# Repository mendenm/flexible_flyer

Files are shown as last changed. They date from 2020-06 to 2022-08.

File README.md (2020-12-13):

# The Paraglider a.k.a. Flexible Flyer

See the [progress log](progress_log.md) to see what is happening.

## NEWS!  
This project has finalized on the name "paraglider" instead of "flexible flyer".  It's the same project! I can't change the name of the git repository.

## Overview

This repository contains a couple of different but closely related, projects.  It is derived from a mix of the [Phoenix v2](https://www.thingiverse.com/thing:1453190), the [Unlimbited Phoenix v3](https://www.thingiverse.com/thing:1674320), and the [Phoenix Reborn](https://www.thingiverse.com/thing:2217431) hands.

* The big part:  fully parameterized scaling of the v2 and Reborn palms, using OpenSCAD.  
	* 	This allows the palms to be scaled independently of the hinges, so that commercial steel pins or nails can be used to make precision, smooth-operating joints.  
	* The parameters allow selection of different options for both hinge pins and for plastic tubing bearings, which make even better joints.  So far, there a designs using:
		* 	 industrial 1/16" dowel pins with Delrin tubing bearings around them
		* 	 3 mm screws with PTFE tubing for bearings
		* 	 Stainless steel finishing nails (deck nails) with PTFE tubing
 	 
		All of these options add between about $0.50 and about $2.00 to the cost of a hand. Materials sources are shown at [Joint Materials](#Joint-Materials)
	
	* The clearance on the tongue-and-groove joints is set independently of the scale of the hand.  This way, hands do not become floppier as they scale up to larger size. Also, by adjusting this spacing, there is room to insert self-lubricating plastics in the joint to lower the friction.  This will improve the grip strength.
* [A new design for supports](#New-support-system) for the big arch on all three of these palms. I am providing a completed STL file for these, along with the OpenSCAD code which converts the basic palm into the supported palm.  These supports are flying supports; they do not touch the baseplate.  They are bridged under the top of the arch, and require very little material or time to print.  They break off easily after printing, and remaining nubs can be sanded off.  
* Repaired meshes for the v2 and Reborn palms.  The meshes were run through [Meshmixer](http://www.meshmixer.com) to remove the support box, and then the remaining holes in the mesh were (mostly) closed up.  The Reborn palm, which is derived from the v2 palm, is rederived using OpenSCAD to make the modifications required.

## Parametric Scaling and modification

This is a parametric adaptation of the Phoenix Reborn hand, that allows the primary components (palm and fingers) to be scaled while holding the sizes of the connecting components (finger pins) constant,  so a standard kit of metal connectors can be used, instead of printing plastic pins to connect everything.  The OpenSCAD files allow one to select sizes for whatever connectors are to be used, and then independently scale the palm and fingers.  The connectors can be metal pins of nails, or 3mm screws.  They can have plastic tubing (Delrin or PTFE) wrapping them inside the holes in the phalanx, resulting in a very smooth-operating bearing.

The palm design is a combination of the Phoenix Reborn palm with the fused-in mesh from the Unlimbited V3 palm. This greatly reduces the number of screws required to assemble the hand.  The palm also has new 'flying supports' which solve the problem of the overhang at the top of the palm arch, without printing large support structures. If the integrated mesh is not needed, it can be disabled in OpenSCAD. 

The whole design here is to provide a flexible toolkit to create locally-appropriate variations of the hand, while letting OpenSCAD handle the scaling issues.  Many things can be commented out of the OpenSCAD code to make variations.  For example, if the fused palm mesh isn't desired, the line which fuses it in can be preceded with an asterisk ('*') which tells OpenSCAD to ignore it.  Also, if the new support structure is desired but conventional printed pins are still being used, all the fancy parametric drilling can be turned off, resulting in a (nearly) conventional Reborn hand.

The Reborn-style hand is being recreated in OpenSCAD from the Phoenix v2 palm, by redrilling the tunnels and slots, since it was possible to repair the mesh for the v2 palm to the point where OpenSCAD considered it valid (after removing the support box in MeshMixer).  It has not been possible to date to repair the Reborn palm mesh to the point at which the OpenSCAD openCGAL geometry libraries consider it valid. The file "palm\_left\_v2\_nobox.stl" contains this modified mesh.  

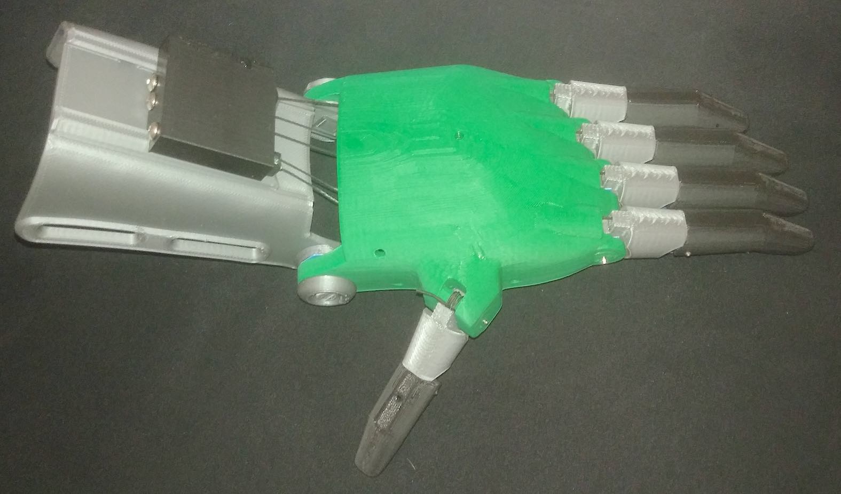
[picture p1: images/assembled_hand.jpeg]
picture of palm and fingers
 

**NOTE**:  any parts not present in the OpenSCAD files are assumed to be obtained from the Phoenix Reborn repository or the Raptor Reloaded repository, which have the gauntlet and other bits.

### Generating the parametric results
You need to run the fingerator.scad to get an STL of a set of fingers at a specific size.  Then run paraglider\_palm\_left.scad to get a hand of the same size, with the same pin specification.  In OpenSCAD, you will unhide the (normally hidden) Customizer window, which will bring up drop-down menus to set the sizes.  I usually start with 130% scale (1.3 size), which is a medium-sized hand.

The fingerator only generates one of each size finger, so for a real hand, these would be duplicated in the slicer to get appropriate numbers.  I would start just by printing one of everything, and experimenting with the parts.  The fingers are much smaller than the palm, of course, so it is not a big issue to print variations on them. Note that if the parts do not fit well, you only have to change the clearance and reprint the phalanges, since they are where the clearances are calculated in.

You also need to run gripper\_box\_pieces.scad to generate the tensioning box scaled for the thermoformed gauntlet.  This result is compatible with simply scaling whippletree\_JD3.stl to the appropriate size in the slicer.

## Joint Materials

Here is a list of sources I am using for the materials.  Variants of most of these should be available from industrial supply houses anywhere in the world. I do not endorse the sources below, but they do have stuff I need.

* 1/16" dowel pins, various lengths
	* pins [McMaster-Carr](https://www.mcmaster.com) SKUs 90145A421, 90145A422, 90145A423, 90145A425, for example. Needs 10 total, including one of the longer ones (depending on hand size) to pin the combined index and middle finger joint.  If a rotary (Dremel, e.g.) tool is available, pins can be easily cut to length.
	* 1/16" ID Delrin bearing tube McMaster-Carr SKU 8627K119, need about 2 inches to do a hand. 

* 3 mm screws
	* Screws are universally available
	* tubing any metric 3mm ID tubing or Imperial 1/8" ID tubing

* Stainless Steel nails (the cheapest option, by far!)
	* for example, [Fastener USA](https://www.fastenerusa.com/nails/hand-drive-nails/finishing/1-1-2-x-15-gauge-304-stainless-4d-finishing-nails-1lb.html).  These can be cut to length.
   * tubing for bearings can be found at (for example) [Fluorostore](https://fluorostore.com/products/fractional-metric-ptfe-fluoropolymer-tubing).  

* Side-load bearings to insert in joints if extra clearance is left in the phalanges can be obtained from [Igus](http://www.igus.com), part number A160T-5-100-G.  This item, for about $13.00, is 1 meter of 100 mm wide, 0.5 mm thick, adhesive-backed self-lubricating plastic tape.  One spool should make between 50 and 100 hands, so it adds no significant cost. Also, part number A160T-5-100 is the non-adhesive variety of bearing material, which is useful for the thermoformed wrist bearing, where there is no need for the adhesive. Use their 'search' field at the top of the page; there is almost no other way to find these on their web store.

## New support system

This support system looks like:
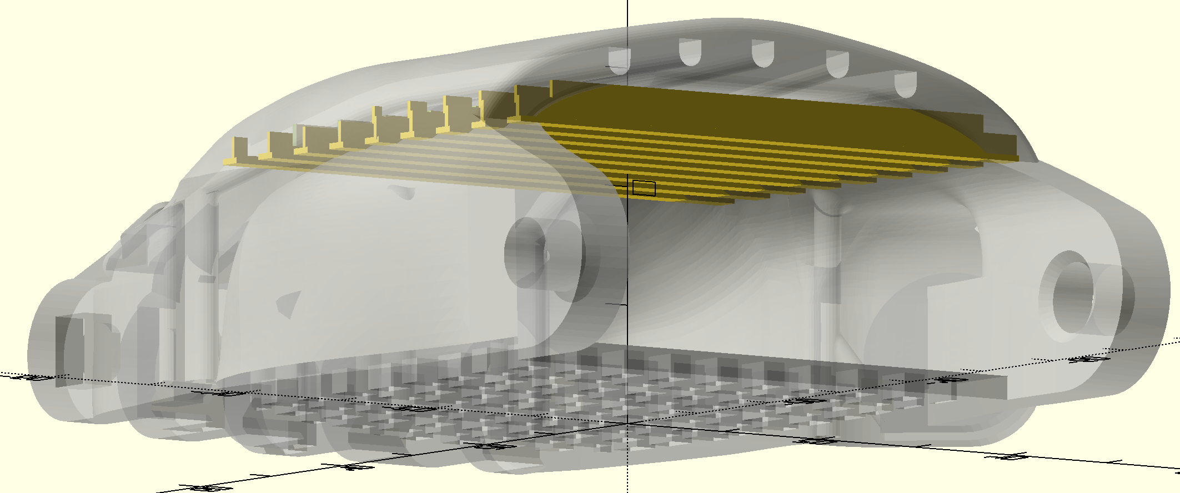
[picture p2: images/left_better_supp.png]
Rendered image of support system
  The goal is a print which is walk-away safe, which can be started, and expected to just work without any close monitoring to make sure the arch finishes safely. If you can print a half-decent bridge, these will work.  It should be printed with quite a lot of cooling, since there is still a significant overhang, but the supports start just low enough that the overhang never becomes dangerous. 

After printing, these supports snap off quite easily.  They leave small 'nubs' on the inside, which sand off very well with a rotary tool such as a Dremel tool with a flap wheel.  They can be removed by hand-sanding, too.

STL Files are provided for left-hand palm of the Unlimbited Phoenix v3, the Phoenix v2, and the regenerated Phoenix Reborn.  Just mirror these in the slicer to get the right-hand version.  Also, an OpenSCAD file for each of these is provided, to allow the supports to be adapted as needed.  The mesh for the Unlimbited palm was regenerated directly from the online Fusion360 source file, to get a higher-resolution mesh.  All of these are designed to be printed flat on the printer bed, with no supports and no raft.

# Notes from Phoenix Reborn README.txt
*Rest of the text blatantly copied from the Phoenix Reborn file*

This is a Remix of the Phoenix Hand & UnLimbited Arm, designed by Albert Fung. This project is a collaboration between e-NABLE Sierra Leone and the Hong Kong Maker Club.

It became apparent in our previous feasibility study that for the 3D printed prosthetics to survive the tropics, we need to remove components that are not well-adapted to hot weather. We therefore set out to replace all the rubber bands in the Phoenix hand.

Palm: We used the One-Arm palm designed by below_cho as out starting point. All the cable tunnels have been widened, the knuckle stumps removed, and a bar is added at the thumb base for tying elastic cord.

Palm mesh: we have modified the thick palm mesh by John Diamond to strengthen the screw holes.

Fingers: Tunnels have been created so an elastic cord can now run all the way from the finger tip up into the palm.

Pins: For snug fitting, some of the pins have been resized and reshaped.

Hope you'll find this new remix useful!

Ed Choi

## Links:

* [e-NABLE Sierra Leone - Facebook](http://www.facebook.com/enablesierraleone)
* [e-NABLE Sierra Leone - CrowdFunding](http://www.GoFundMe.com/enablesierraleone)
* [Albert Fung - designer](http://albertfung.ca)
* [Hong Kong Maker Club - collaborator](https://www.facebook.com/hongkongmakerclub/) 
* [Raise3D HK Printer - manufacturing](https://www.facebook.com/raise3dhk/)
* [Printact 3D Printer - prototyping ](http://www.printact.co)

## Print Settings

* Rafts: No
* Supports: No
* Infill: 30%
* Walls/top/bottom: 3
* Layer height: 240-320 µm from an 0.4 mm nozzle.  If adaptive layers are available, making the very top of the hand have smaller layers will result in a smoother top.

## Notes: 

For a wrist-powered prosthetic hand, please use the [Reborn Hand thermal gauntlet](http://www.thingiverse.com/thing:864030).
 and tensioner/tensioner pins from the [Raptor Reloaded](http://www.thingiverse.com/thing:596966). 

For an elbow-powered prosthetic arm, please use the Reborn palm with the "forearm" and bicep "cuff" from the UnLimbited Arm (see link). There is a glitch in the Thingiverse Customizer, so you will need to set the UnLimbited "hand length" to at least 145mm. Otherwise the forearm wrist joint would not be wide enough to fit into the palm.
 
http://www.thingiverse.com/thing:1672381
http://www.teamunlimbited.org/the-unlimbited-arm-20-alfie-edition-current/

We printed the Reborn hand at 124% and used it with parametric forearm, cuff and tensioner pins from the UnLimbited Arm(v2.0). From our field experience, the UnLimbited Arm cuff pins are not stronger enough to hold the elbow in place for very long. So we advice everyone to use Chicago/binding screws (glued) instead.

Scaling the ReBorn Hand parts at 124% would give you:

Palm width (widest): 80mm
Wrist joint (outside): 75mm
Wrist joint (inside): 64mm

## Additional materials:

* [Braided fishing line - 80lb.](http://www.ebay.com/itm/KastKing-SuperPower-Braided-Fishing-Line-330-yds-1100yds-SELECT-LB-TEST-/190909992257?var=&hash=item2c731f4d41:m:m6k91tkQ1bIzQbS8tDpHzaQ)
* Elastic cords - 1.5mm - for hands printed at 100% or above
* Screws - for tensioner block - Hands printed at 124%: 
single thread woodscrew 3.0 x 30mm
* Screws - for palm mesh printed at 124%:
Reassure R2 - full thread woodscrew 3.0 x 16mm
* Silicone fingertip grips - Tipper Lee, and superglued to secure them to the fingers
* Velcro - 1 inch thick double-sided
* [Adhesive Foam - 5mm thick](https://www.amazon.co.uk/Self-Adhesive-various-including-padding-Outfitting/dp/B002GUB9R0/ref=sr_1_5?s=sports&ie=UTF8&qid=1491140349&sr=1-5)
* 13mm binding screws for the elbow joints (use superglue or Loctite to prevent loosening). 
* [Loctite 243 seal thread](http://www.ebay.com/itm/121826873262?_trksid=p2057872.m2749.l2648&ssPageName=STRK%3AMEBIDX%3AIT)

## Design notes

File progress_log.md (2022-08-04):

# The Paraglider Progress Log
## Summer 2022
Wow! Just Wow.  An Eagle Scout project was developed to  produce detailed documentation for this, in the form of a PDF user manual, and a brief video to show how to work with OpenSCAD on these files.  Thanks to Peter Ilyin and his crew!  See the [manual](Instruction\_manual\_rev2.pdf) and [video](images/Instructional\_Video\_Trim.mp4).

* *Peter Ilyin* - Project Lead, Eagle Scout Candidate
* *Jackson Rodgers* - General Volunteer, Volunteer Coordinator, Technical Support Volunteer, Technical Writer, and Illustrator.
* *Leonard Katowitz* - General Volunteer, Printer Assistance, Photographer, and Illustrator
* *Dean DeSeve* - General Volunteer, Technical Writer, Photographer, and Illustrator
* *Mark Dorazelski* - General Volunteer, Technical Writer,  and Technical Consultant
* *Jasper Mosely* - Technical Consultant, and Digital Design Consultant
* *Albert Z* - General Volunteer, Instructions Tester
* *Thomas H* - General Volunteer, Instructions Tester
* *Dalton S* - General Volunteer, Instructions Tester
* *Indigo S* - General Volunteer, Instructions Tester
* *Chris S* - General Volunteer, Instructions Tester
* *Rick Y* - General Volunteer, Instructions Tester
 
## Mid-December 2020
### Wrist joint
The work on a wrist joint using an m3 screw instead of a plastic pin
is complete.  The joint has a conical thrust/axial bearing printed
in, so the screw is not the actual bearing.  It can be assembled
without any bearing material, or can either have something like
polypropylene sheet inserted to lower friction, or it can use the
non-adhesive Igus A160T-5-100 plastic, described in the materials list.  If using the
Igus plastic, I have included an option to print a thermoforming jig
which allows the plastic to be heated, and then stamped and drilled
using the jig.

### Labeling text
To allow hands to be traced and recorded, I have added the ability
to print 3 lines of text on the inside of the hand. These might
include the maker name, a serial number, and a date.
Whatever you want...

### Here it is
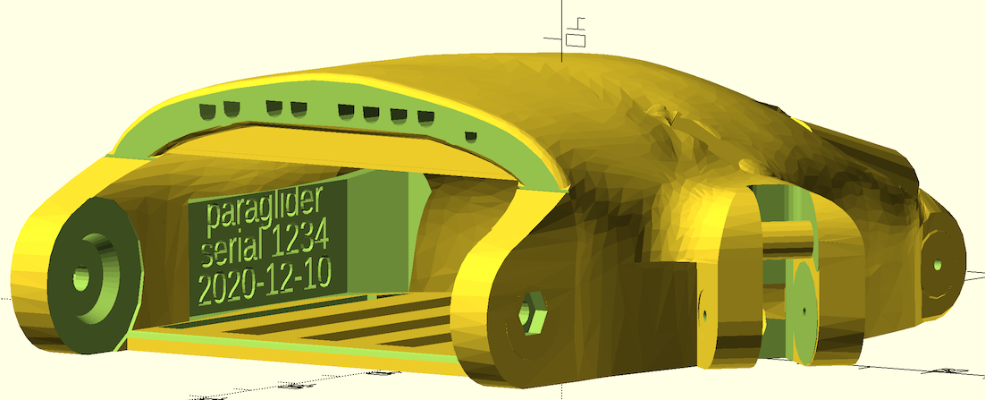
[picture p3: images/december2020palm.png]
Hand with new bearings and text

This shows the current wrist and text design.

## Early November, 2020

### Name change (sort of) to "paraglider"
It has been decided that this project will adopt the "paraglider" name, since "flexible flyer" makes it appear it might be a flexure-joint based project.  Some files and materials will keep the old name, though.

### New!  Unlimbited V3 palm 
It is now also possible to build the parametric palm against the [Unlimbited Phoenix V3](https://www.thingiverse.com/thing:1674320)  palm, which is somewhat different.  Everything works almost the same, but the passages (especially the thumb string) are quite different. Everything should be compatible, although I have not yet tested the thumb.  The positioning of the thumb socket is different on this palm, and it may require a slightly different parametric scaling of the thumb. Use paraglider_palm_unlimbited_v3.scad and its customizer script to use this.

### Reborn palm progress
Much cleanup has been carried out on the palm based on the Phoenix Reborn project.  

## Later October, 2020
The entire 'fingerator' module has been replaced. The original used a slice off of the Phoenix finger meshes to start with, and edited from there.  The new fingers are entirely OpenSCAD objects.  
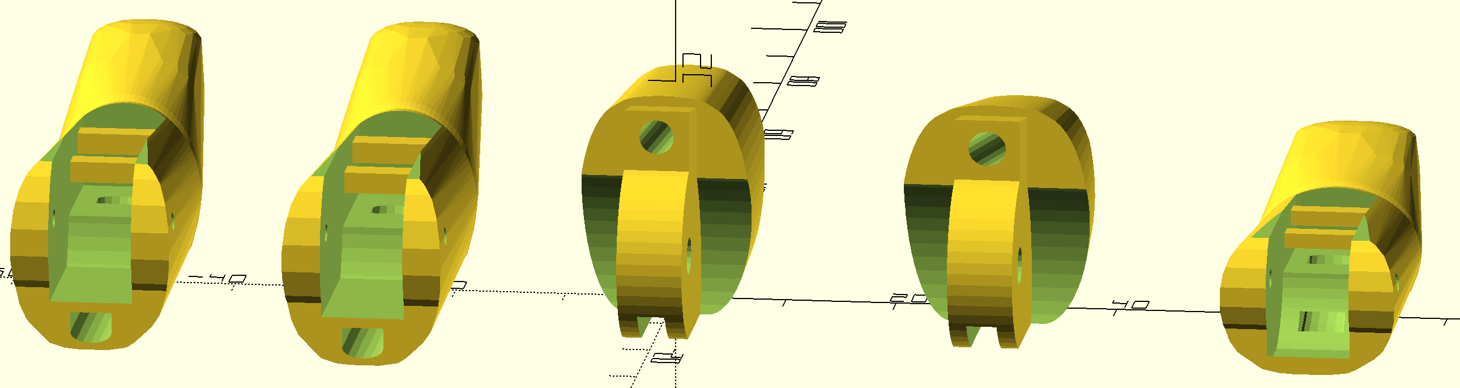
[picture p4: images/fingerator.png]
Rendered image of new fingers
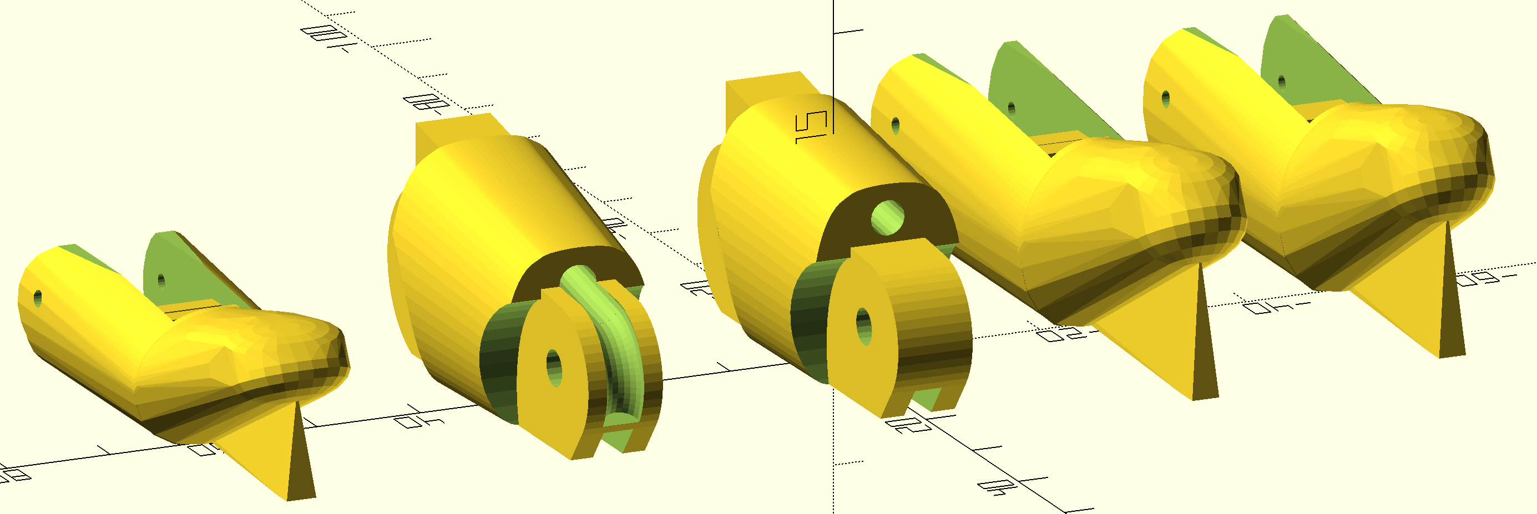
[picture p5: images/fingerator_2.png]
Rendered image of new fingers
   They have the following improvements:

* A 'keel' on the overhang to make it _really_ easy to print.  Even without very good cooling,  the distal segment overhang comes out smooth. The keel is easy to break off, and sand the stub away.
* The entire path for the elastic is covered, resulting in better aesthetics. The elastic now passes through from the top of the finger to the bottom, where it gets tied.
* There is a channel to guide the elastic so that it can be inserted in most cases without any  sort of leader to push or pull it through.
* There are two bars under each finger to tie things to, one for the string and one for the elastic.

The goal of these efforts is to produce a hand which gives as stronger grip with less effort from the user, to assist people who do not have a lot of wrist strength.

Here is a picture of an assembled finger, showing the blue Igus self-lubricating tape, the off-white bearing tubing inside a joint, and the assembled joint with a 1/16" steel pin.
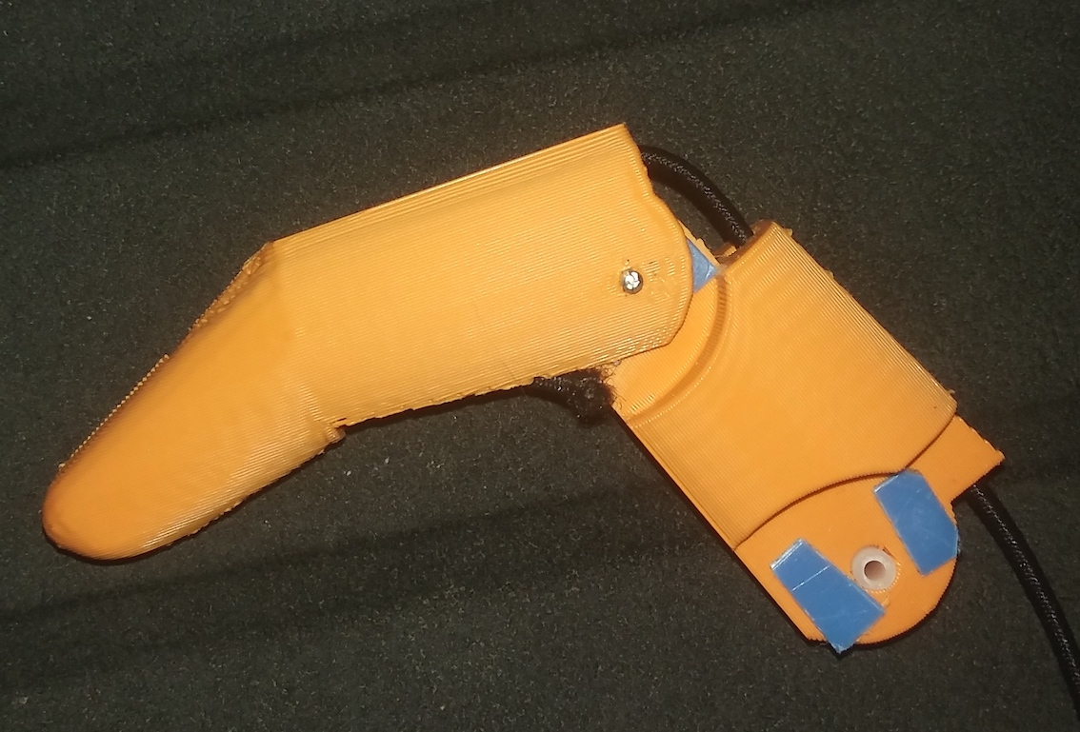
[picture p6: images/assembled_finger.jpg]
 

## October, 2020 update
There is a new OpenSCAD file, paraglider\_palm\_new\_channels.scad.  This file has a better mechanism for filling in the old string channels to get rid if various voids, etc.  It then implements an entirely new system for the channels.  There are two channels for each digit (except the thumb): one for the string and one for the elastic return band.  This should make it easier to thread, using a piece of wire as a leader to puller the strings through. It should also eliminate drag between the two lines. 
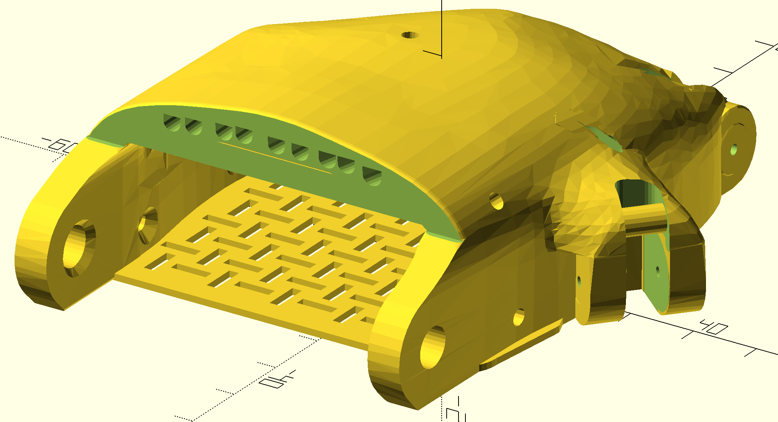
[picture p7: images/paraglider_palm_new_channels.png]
Rendered image of new channels


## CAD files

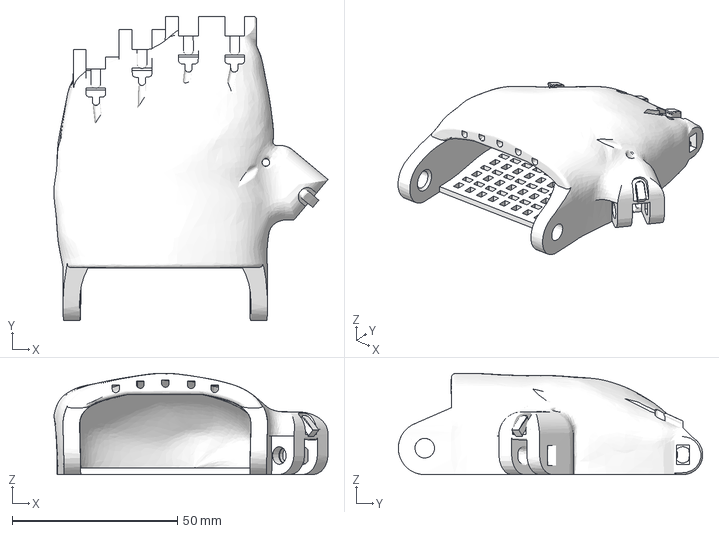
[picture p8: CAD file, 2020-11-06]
files/palm_v3.3mf
82.8 x 92.0 x 30.6 mm

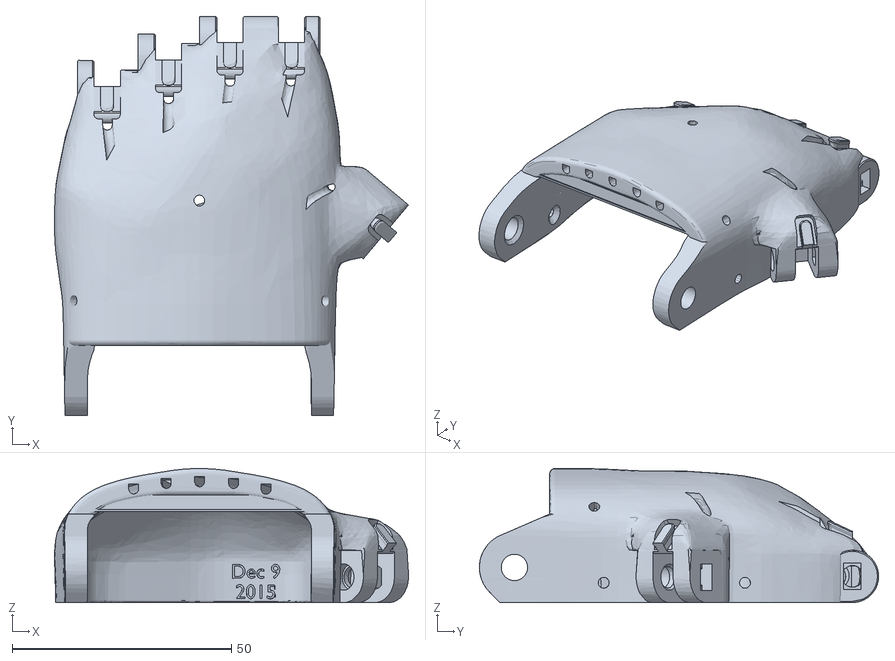
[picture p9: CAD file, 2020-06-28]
files/Phoenix_v2_new_supports.stl
80.6 x 91.0 x 30.6

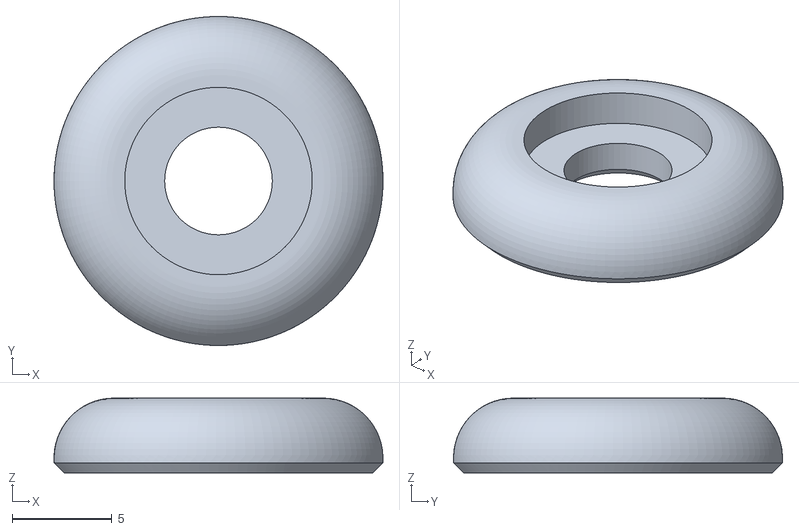
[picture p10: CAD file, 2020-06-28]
files/Reborn_elbow_pin_cap.stl
16.5 x 16.5 x 3.75

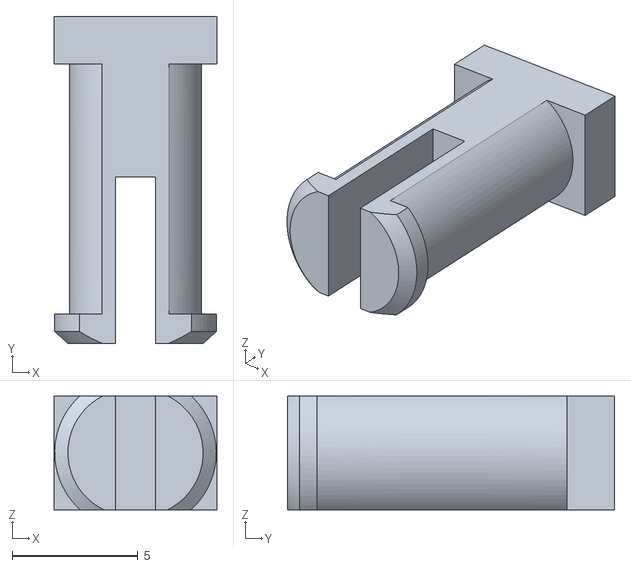
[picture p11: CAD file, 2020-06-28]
files/Reborn_wrist_pin.stl
6.46 x 13.0 x 4.51

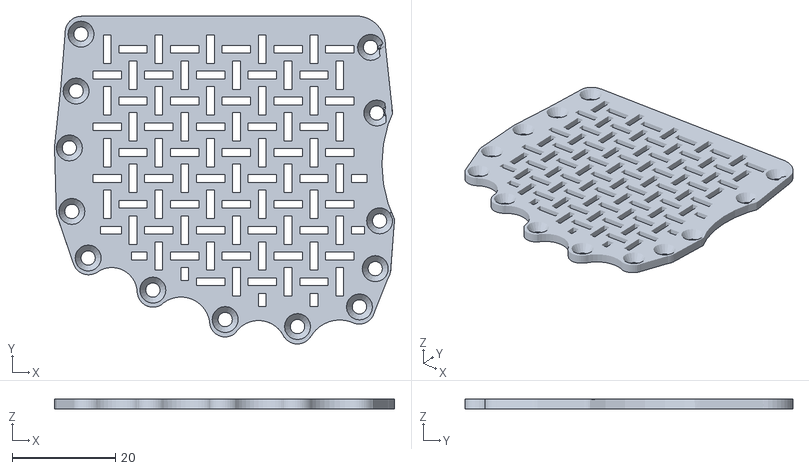
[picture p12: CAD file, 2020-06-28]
files/reborn_palm_mesh_thick_left.stl
65.8 x 63.4 x 2.00

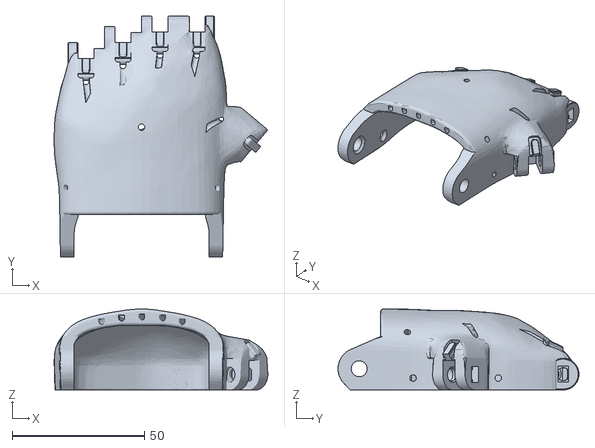
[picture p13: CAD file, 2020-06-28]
files/palm_left_v2_nobox.stl
80.6 x 91.0 x 30.6

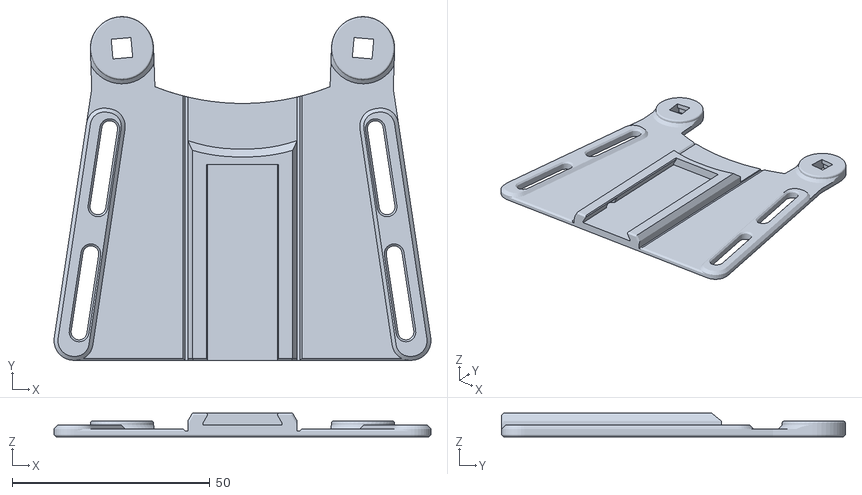
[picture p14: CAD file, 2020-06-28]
files/thermo_gauntlet_two_strap_one_row.stl
95.4 x 87.0 x 6.00

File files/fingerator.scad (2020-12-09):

/*
Parametric Finger Generator for Phoenix-reborn hand converted to paraglider/flexible flyer.
This takes a fully OpenSCAD-modelled finger, based on the general geometry of the Phoenix Reborn,  
in a manner that scales the holes to a chosen size indepenedent of the finger size.
This allows one to use a wide variety of commercial metal fasteners in lieu of 3d printed pins
to create the pivots for fingers.  

The designs in the default version of this files are set up
to use 3mm screws, 1/16" steel pins, or 13 ga (0.092") (USA) nails, with a plastic tubing
bearing on the outside to make it move smoothly.  The pins and nails may not need the tubing,
and parameters can be adjusted to make this the case. 

By manually adjusting the lines
  pivot_dia= pivot_array[pivot_size_index];
  pivot_pin_dia=pin_array[pivot_size_index];
at the bottom, to put in actual numbers instead of the pre-packaged values,
almost any geometry can be created for regions with different (e.g. metric) pins or nails.

Note that the parameters can be adjusted for your printer tolerances.  Mostly, you probably
only have to reprint the phalanx parts to adjust the joint quality, since they are the part that 
includes the hole for the pivot, and that has a clearance for the slots.  
The line
  nominal_clearance=0.6;
sets the looseness of the slots for the joints; making it smaller makes joints tighter.
Since this is cut parametricall after the scaling is done, once you have found a good value
for your printing setup, it should work for all sizes of hands, instead of getting looser
as the hands get bigger.

Marcus Mendenhall, 5 June, 2020, Germantown, Maryland, USA

*/

// size of fingers. should match scale of hand they are being printed for.
global_scale=1.25; // [1.0:0.01:2.0]
// Clearance on sides of tabs.  increase for looser fit. This only affects the phalanges, so a bad fit does not require reprinting  anything else.
nominal_clearance=0.5; // [0.1:0.01:3]

/* [Items to print] */
print_long_fingers=true; 
print_short_fingers=true; 
print_finger_phalanx=true; 
print_thumb=true;
print_thumb_phalanx=true; 

/* [Igus Bearing Material] */
bearing_pocket_diameter=0; // [0,5,7,9,11,13,15]
bearing_pocket_depth=0.4; // [0.2:0.05:0.6]

/* [Pin Style Selection -- select one] */
// choose the type of steel pin for the joints
pin_index=1; // [0: 3mm screws, 1: 1/16 inch pins with bearing, 3: 1/16 pins with no bearing, 2: 13ga finishing nails] 
// tie string onto another steel pin if true, otherwise use plastic bars
pins_for_string=false; // [false:plastic bars for string, true: steel pins for string]
    
// Extra clearance for pins to adjust for printer differences to make pins reasonably tight fits. Note that this affects all joints, so it should be pre-tested on something small like a finger in advance.
pin_diameter_clearance = 0; // [-1:0.01:1]

screws = (pin_index==0);

/* [Hidden] */
// 3mm screws with 3/16" OD delrin rod
pivot_dia_3mm_screw=25.4*(3/16)+0.25; // 3/16" OD delrin tubing with a little clearance since they were too small otherwise
pivot_pin_dia_3mm_screw=3+0.1; // 3 mm screws

// 1/16" pins with 1/8" OD delrin rod
pivot_dia_8th_delrin=25.4*(1/8)+0.25; // 1/8" OD delrin tubing with a little clearance since they were too small otherwise
pivot_pin_dia_16th_pin=25.4*(1/16)+pin_diameter_clearance; // 1/16" steel pin
// with no delrin tubing, leave extra clearance for holes in phalanges for pins
pivot_pin_dia_16th_pin_clearance=pivot_pin_dia_16th_pin+0.3;

// 13-gauge nails
// https://www.fastenerusa.com/nails/hand-drive-nails/finishing/2-x-13-gauge-304-stainless-6d-finishing-nails-1lb.html
// and 3/32" ID/ 5/32" OD PTFE tubing
// https://fluorostore.com/products/fractional-metric-ptfe-fluoropolymer-tubing
// part number F015137
pivot_dia_13ga_nail=25.4*(5/32)+0.25; // 5/32"" OD PTFE tubing with a little clearance since they were too small otherwise
pivot_pin_dia_13ga_nail=25.4*0.095+pin_diameter_clearance; // 13 ga nail

pivot_array=[pivot_dia_3mm_screw, pivot_dia_8th_delrin, 
    pivot_dia_13ga_nail, pivot_pin_dia_16th_pin_clearance, ];
pin_array=[pivot_pin_dia_3mm_screw, pivot_pin_dia_16th_pin, 
    pivot_pin_dia_13ga_nail, pivot_pin_dia_16th_pin,  ];

pivot_size_index=pin_index;

pivot_dia= pivot_array[pivot_size_index];
pivot_pin_dia=pin_array[pivot_size_index];


/* [Misc] */
// size fo m3 standard nut across flats
nut_size=5.5; // m3 nut across flats, fairly tight fit

bolt_head_dia=5.5+0.3; // loose clearance for m3 bolt head
nominal_slotwidth=6+0; // make an equation to hide from customizer
adjusted_tabwidth=nominal_slotwidth-nominal_clearance/global_scale;
adjusted_slotwidth=nominal_slotwidth;

initial_rotation=33.5+0; // hidden from customizer

module fingertip() {
    cyl_1_dia_1=11;
    cyl_1_dia_2=9;
    cyl_1_hgt=15;
    cyl_1_rot=atan((cyl_1_dia_1-cyl_1_dia_2)/cyl_1_hgt/2);

    sph_1_dia=cyl_1_dia_2-2;
    scale([1,1.15,1]) hull() {
        translate([0,cyl_1_hgt/2,(cyl_1_dia_1+cyl_1_dia_2)/4]) rotate([-90-cyl_1_rot,360/20/2,0]) 
            cylinder(d1=cyl_1_dia_1, d2=cyl_1_dia_2, h=cyl_1_hgt, center=true, $fn=20);
        for(dx=[-1,1]*0.5) translate([dx,cyl_1_hgt+2.4,sph_1_dia*0.8/2-0.0]) scale([1,1,0.8]) 
            sphere( d=sph_1_dia,$fn=20);
        for(dx=[-1,1]*0.5) translate([dx,cyl_1_hgt,sph_1_dia*0.4/2]) 
            rotate([-40,0,0]) scale([1,1,0.4]) translate([0,-1,13]) 
            sphere( d=sph_1_dia,$fn=20);
        for(dx=[-1,1]*0.3) translate([dx,0,0]) 
            translate([0,11,8.1]) rotate([-10,0,0]) scale([1,1,0.5]) sphere(d=8, $fn=20);
        rotate([90-initial_rotation,0,0]) translate([0,7,0]) scale([0.85,1,1]) 
        rotate_extrude(angle=180, $fn=90) translate([5,0]) circle(d=3, $fn=20);
    }
}

module carpal() {
    translate([0,-5.4,10.5]) rotate([-90-initial_rotation,0,0]) hull() {
        translate([0,0,-16]) linear_extrude(height=0.1) hull() {
                translate([ 4.,0,0]) scale([0.3,1]) circle(d=12);    
                translate([-4.,0,0]) scale([0.3,1]) circle(d=12);
                translate([0,-7.0]) scale([1,0.2]) circle(d=16*0.4);
                translate([0, 7]) scale([1,0.2]) circle(d=16*0.4);
        }
        translate([0,6,10]) linear_extrude(height=0.1) 
            projection(cut=true) rotate([90+initial_rotation,0, 0]) fingertip();
    }
}
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

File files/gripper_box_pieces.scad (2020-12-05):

// parts for flexible-flyer parametric variant of Phoenix Reborn

// this should match the scale of the hand and gauntlet
global_scale=1.25; // [1:0.01:2]

// this sets how much clearance is on the dovetail.  It shouldn't depend on the scale
slide_clearance=0.2; // [0:0.01:0.5]

// The (approximately) root diameter of the screw thread for a nice fit
screw_thread_dia=2.8; // seems to work for m3
screw_clearance_dia=screw_thread_dia+0.5;
// diameter of screw head
screw_head_dia=5.5; // m3 screw
// distance between edge of screw heads and slider rail
screw_head_clearance=1.0; // minimum distance of screw heads above slider rail

module slide(grow) {
    // make a scalable slide profile, inset by the specified amount for clearance
    union() {
        hull() {
            translate([0,6.65]) square([20+grow,0.70], center=true);
            translate([0,4.3]) square([17+grow,0.5], center=true);
        }
        translate([0,4.5]) square([17,5], center=true);
    }
}

module box() {
    cl=slide_clearance/global_scale;
    difference() {
        linear_extrude(height=28) union() {
          square([30,8], center=true);
          slide(grow=-cl);
        };
        whip_box_x=11.2+cl;
        whip_box_y=5;
        
        translate([-1.8,6.0-whip_box_y/2+cl,22]) 
            cube([whip_box_x,whip_box_y,40], center=true);


        piv_box_x=22.0+cl;
        piv_box_y=5.4+cl;
        
        translate([-3,2.5-piv_box_y/2,22]) 
            cube([piv_box_x,piv_box_y,40], center=true);
        
        thumb_pin=4.8+cl;
        translate([11.5,0,22]) 
            cube([thumb_pin,thumb_pin,40], center=true);
        
        
        for(dx=[[11.5,0,0],[-4.6,4.2,0],[1,4.2,0]]) translate(dx)
            cylinder(d=screw_clearance_dia/global_scale+.25, h=40, $fn=20, center=true); 
    }
}

module thumb_tensioner() {
    // translate([-15.0,69.8,-25.5]) import("thumb_v2_tensioner_pin.stl", convexity=10);
    translate([0,0,2.4]) difference() {
        rotate([-90,0,0]) intersection() {
            cube([4.8,4.8,20.5], center=true);
            rotate(45) cube([4.8*sqrt(2)-0.5, 4.8*sqrt(2)-0.5, 45], center=true);
        }
        translate([0,-3,0])
            rotate([90,0,0]) 
                cylinder(d=screw_thread_dia/global_scale, h=15, center=true, $fn=20);
        // translate([0,8,0]) cylinder(d=2, h=15, center=true, $fn=20);
        translate([0,10.3,0]) scale([1,1.2,1])
            rotate([0,90,0]) rotate_extrude(angle=180, convexity=10, $fn=50) 
                translate([-2.5,0]) circle(d=2.5, $fn=20);
    }
            
}

module pivot() {
    translate([0,0,3.5/2]) {
        difference() {
            translate([0,0,0]) cube([11,20,3.5], center=true);
            for(dx=[-2.8,2.8]) translate([dx,0,0]) rotate([90,0,0]) 
                cylinder(d=screw_thread_dia/global_scale, h=50, center=true, $fn=20);
        }
        translate([-1.1,3,1.74]) difference() {
            cylinder(d=6.5, h=5, $fn=20);
            scale([1,0.3,1]) translate([0, -10*sqrt(2)/2,0]) rotate(45) cube([10,10,12], center=true);
        }
    }
}

module whipple_tree() {
    // %import("whippletree_JD3.stl", convexity=10); 
    thickness=5.4-slide_clearance/global_scale;
    ht=thickness/2;
    difference() {
        linear_extrude(height=thickness) difference() {
            hull() {
                $fn=20;
                translate([0,-3.8,0]) circle(d=7);
                translate([6.3,1,0]) circle(d=8);
                translate([-6.3,1,0]) circle(d=8);
            }
            difference() {
                translate([0,-1]) circle(d=9);
                translate([0,-9]) rotate(45) square(5);
            }
        }
        for(dx=[-1,1]*5.3) translate([dx,5.2,ht]) scale([0.7,1,1])
            rotate_extrude(angle=360, $fn=50) translate([5,0]) 
                scale([1/0.7,1]) circle(d=2, $fn=16);
    }
}

scale(global_scale) translate([-5,-15,0]) rotate(0) pivot();

scale(global_scale) translate([5,-15,0]) rotate(0) thumb_tensioner();

scale(global_scale) box();

translate([0,15*global_scale,0]) rotate(180) scale(global_scale) whipple_tree();

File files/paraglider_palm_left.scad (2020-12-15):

inch=25.4*1; // hidden from customizer by equation, useful for pins
/* [Main setup] */
// size of hand relative to tiny 100% model
overall_scale=1.25; // [1.0:0.01:2.0]
// mirrored for right-hand?
mirrored=false; // [false:left, true:right]
// an identifying string for this hand, i.e. build date, builder, serial, etc. (15 characters/line max)
serial_line1="paraglider"; // 15
serial_line2="serial 1234"; // 15
serial_line3="2020-12-10"; // 15
// include a stamping die for thermoforming 0.5mm thick Igus bearing plastic for wrist
include_wrist_stamping_die=true; // [true: die included, false: no die]
/* [Structural parameters] */
// size of pivot pins
pivot_size=1.5875; // [1.5:metric 1.5, 1.5875:16th inch, 3.0:3mm screw]
// extra clearance for pivots to adjust for printer tolerances
pivot_extra_clearance=0; // [-0.5:0.01:0.5]
// drill holes for steel pins
pins=true; // [1:steel pins, 0: plastic pins]
// create plugs for steel pins, or leave old holes for plastic pins 
plugs=true; // [1:steel pins, 0: plastic pins]
// include fused-in palm mesh?
include_mesh=1; // [0:standard mesh, 1:simplified mesh]
// include nice covers for knuckles
include_knuckle_covers=true;
// set size of channels for strings
string_channel_scale=0.9; // [0.5:0.05:1.0]
// set size of channels for elastic
elastic_channel_scale=0.9; // [0.5:0.05:1.5]
// even if using steel pins on the fingers, use plastic pins on the wrist if old-style
old_style_wrist=false; // [true:old style, false:m3 wrist screws]
/* [Development] */
// make main object a ghost for debugging
main_ghost=false; // [1:ghost, 0:real]
// leave out string channels in preview, for much faster viewing
fast_preview=false;

use <pipe.scad>
module channel(waypoints, shapescale=1, bendradius=5, 
    fix_translation=true) {
    // the bends work best if the primary length is along 'x' here,
    // but the hand is along 'y', 
    // so we will adjust the coordinates, 
    // and then re-rotate the whole thing
    shape=[[-1.5,-1],[1.5,-1],
        each 1.5*[for(th=[0:30:179]) [cos(th), sin(th)]]
    ]*shapescale;
    path=[for(w = waypoints) 
        [0,[w[1],-w[0],w[2]],1,
            -90+((len(w)==4)?w[3]:0)]];
    // note: do a translation so that the curved _bottom_ of the pipe is
    // invariant under scaling, relative to its position when scale=0.9.
    // This is for historical continuity
    y_trans=fix_translation?1.5*(shapescale-0.9):0;
    translate([0,0,y_trans]) rotate(90) multi_pipe([shape], 
        smooth_bends(path, 2, bendradius));
}

module supports() {
    for(dy=[-29:5:10]) translate([0,dy,0]) {
        translate([-7,0.5,21]) cube([52,2,0.5],  center=true);
        translate([-7,0,22]) cube([52,0.4,2],  center=true);
        // translate([-7,0,22]) cube([45,0.4,3],  center=true);
        translate([-7,0,23]) cube([45,0.4,3],  center=true);
        translate([-7,0,23]) cube([30,0.4,3],  center=true);
    }
}


// plug up all holes and slots which need to be parametric
module chamfered_cylinder(d=20, h=20, center=true)
{
    union() {
        cylinder(d=d, h=h-1, center=true);
        translate([0,0,h/2-.51]) cylinder(d1=d, d2=d-1, h=0.5);
        translate([0,0,-h/2+0.01]) cylinder(d1=d-1, d2=d, h=0.5);
    }
}

slot_dx=[[[10,0,0],0],[[-4,0,0],0],[[-18,-4,0],0],
    [[-32,-10,0],0]];

pin_coordinates=[
    [[-35.4,-38,8],[0,90,0]], //left wrist
    [[20.68,-38,8],,[0,90,0]], // right wrist
    [[6.6,39.5,6.0],[0,90,0]], // index and middle finger
    [[-16,35.5,6.0],[0,90,0]], // ring finger
    [[-29.5,29.5,6.0],[0,90,0]], // pinky
    [[31,0,6.0],[0,90,50]], // thumb

];

module knuckles() {
    // re-insert clean finger stops
        for(dx=slot_dx) translate(dx[0]+[3.7,38.5,12.5]) 
            rotate([90,0,-90+dx[1]]) linear_extrude(height=8, center=true)
                hull() {
                    translate([3,0]) square([0.1,3]);
                    translate([0,0.5]) circle(1, $fn=10);
                };
    // smooth covers for knuckles
    // compute individul offsets to place them nicely
    cover_dx=[
        [[-1,-4,-2.25],[-115,0,-3],3],
        [[0,-2,.75],[-125,0,0],2],
        [[1,-3,-0.25],[-120,0,3],2],
        [[1,-4,-2.35],[-115,0,3],3]
    ];
                
    if(include_knuckle_covers) for(idx=[0:3]) translate(cover_dx[idx][0]+slot_dx[idx][0]+[3.7,25,23]) {
        intersection() {
            rotate(cover_dx[idx][1]) difference() {
                hull() {
                    scale([1,0.5,1]) cylinder(d=10, h=0.1, $fn=20);
                    translate([0,0,19]) cylinder(d=10,h=0.1, $fn=20);
                }
                hull() {
                    translate([0,0,-1]) scale([1,0.5,1]) cylinder(d=8, h=0.1, $fn=6);
                    translate([0,0,21]) cylinder(d=8,h=0.1, $fn=6);
                }
                translate([0,10,-1]) cube([20,20,50], center=true);
            }
            translate([0,cover_dx[idx][2],0]) cube([15,30,20], center=true);
        }
    }
}

module mesh(mesh_thickness=2) {
    holes=[ // plug all screw holes
            [8.7,62.6], [7.7,51.5], [6.5,40.5], [6.9,28.4],
            [10.1,19.3], [22.3,13], [36.2,7.4], [50.4,5.9], [62.3,9.6], 
            [65.6, 17.1], [66.4,26.4], [66.0,47.1], [64.7, 60.0], 
        ];
    
    // convenient aliases
    m2=mesh_thickness/2;
    m4=mesh_thickness/4;
    m1=mesh_thickness;
    
    for(dy=[-30:10:20]) translate([-7,dy,(dy==-30)?m2:m4])
        cube([60,5,(dy==-30)?m1:m2], center=true);
    for(dx=[-20:10:20]) translate([-7+dx,-1,3*m4])
        cube([5,62,m2], center=true);

    translate([-43.6,37.1,0]) scale([1,-1,1]) // flip chirality 
        for(xy=holes) translate([each xy, 0.001]) cylinder(d=3.5, h=8, $fn=16);
}

module do_supports() {
    children(); 
    for(dy=[-29:5:10]) translate([0,dy,0]) {
        translate([-7,0.5,21]) cube([52,2,0.5],  center=true);
        translate([-7,0,22]) cube([52,0.4,2],  center=true);
        // translate([-7,0,22]) cube([45,0.4,3],  center=true);
        translate([-7,0,23]) cube([45,0.4,3],  center=true);
        translate([-7,0,23]) cube([30,0.4,3],  center=true);
    }
}


module do_mesh() {
    if(include_mesh==1) 
        union() {
            children();
            mesh();
        }
    else children();
}

module rounded_cutter(width=6, radius=1.5, height=20) {
    linear_extrude(height=height, center=false) 
    hull() {
        translate([0,-20]) square([width,1], center=true);
        translate([-width/2+radius,5]) 
            circle(r=radius, $fn=20);
        translate([ width/2-radius,5]) 
            circle(r=radius, $fn=20);
    }    
}

module plug_old_channels() {
    translate([-28.4,-49.5,22]) channel(
        [ [6.2,19,4.1], [4,40,3.5],[2.9, 47.5, 3.1],  [1.9,55,1.4], 
        [1.15, 62.5, -0.4,-20],  
        [0.8,70, -4.4,-20], ],
        shapescale=1.2, fix_translation=false
    );

    translate([-14.5,-43,24.5]) channel(
        [ [-0.5,13,3], [0,40,3.1], [0,55,1.2],[0.4, 63, -0.9,-10],  [0.8,68, -4.5,-10] ],
        shapescale=1.2, fix_translation=false   
    );

    translate([-0.3,-39,25.5]) channel(
        [ [-7,9,2.2], [-3.5,40,1.8], [-2.75, 47.5, 1.8],  [-2,55,1.0], [-1,64,-1.2], [0,69, -5],  ],
        shapescale=1.1, fix_translation=false      
    );    

    translate([13.5,-39,23.5]) channel(
        [ [-13.2,9,3.7], [-8.5,30,3.5], [-6.5,40,3], [-4.75, 47.5, 2.7], [-2.3,60,-0.5], 
        [-0.2,69, -5.5], ],
        shapescale=1.1, fix_translation=false          
    );

    translate([21.2,-39,22]) channel(
        [ [-13.5,9.3,4], [-10.5,30,3,5], [-8.4,39,3.1,15], [-3,44,0,35], [2,46,-5,50]  ],
        shapescale=1.2, bendradius=10, fix_translation=false          
    );

    // fix ugly bend
    intersection() {
        union() {
            translate([21.2,-39,22]) channel(
                [ [-13.5,9.8,4], [-10.5,30,3,5], [-8.4,39,3.1,15], [-1.7,44,0.5,35], [2,46,-5,50]  ],
                shapescale=1.3, bendradius=10, fix_translation=false          
            );
            translate([20,7,25]) rotate([30,-30,0]) translate([-2,-3,-2]) cylinder(d=5,h=12, $fn=20, center=true);
        }
        translate([9.8,0,12]) rotate([85,0,-5]) cylinder(d=30,h=20, $fn=50, center=true);
    }
    translate([23.5,6.5,0.05]) cylinder(d=4.5, h=18.5, $fn=20); 
 
    for(v=[[13.5,31,18], [-0.5,31,21.0], [-14.2,27,20],  [-28.5,21,18],
        
        ]) translate([v.x,v.y,0]) cylinder(d=4,h=v.z,$fn=20);
}

module final_bend(angle=90) {
    translate([0,-3.5,0]) rotate([90,0,90]) rotate_extrude(angle=angle, $fn=40, convexity=10)
        translate([5,0]) square([3,3], center=true);
}
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

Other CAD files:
files/Unlimbited_v3_with_supports/Unlimbited_v3_palm_left_f360.stl
files/paraglider_palm_left_tensor.scad
files/UnLimbited_Arm_paraglider_v2.1.scad
files/Unlimbited_v3_with_supports/Unlimbited_v3_left_better_supp.scad
files/paraglider_palm_unlimbited_v3.scad
files/paraglider_palm_unlimbited_v3_tensor.scad
files/pipe.scad
files/segmented_pipe_tensor.scad
files/thermo_gauntlet.scad

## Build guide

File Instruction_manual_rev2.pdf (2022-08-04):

# Paraglider Prosthetic Hand

# Assembly Instructions and Guidelines

## Link to Github: https://github.com/mendenm/flexible_flyer

# Paraglider Prosthetic Hand

# An Example of a Completed Hand

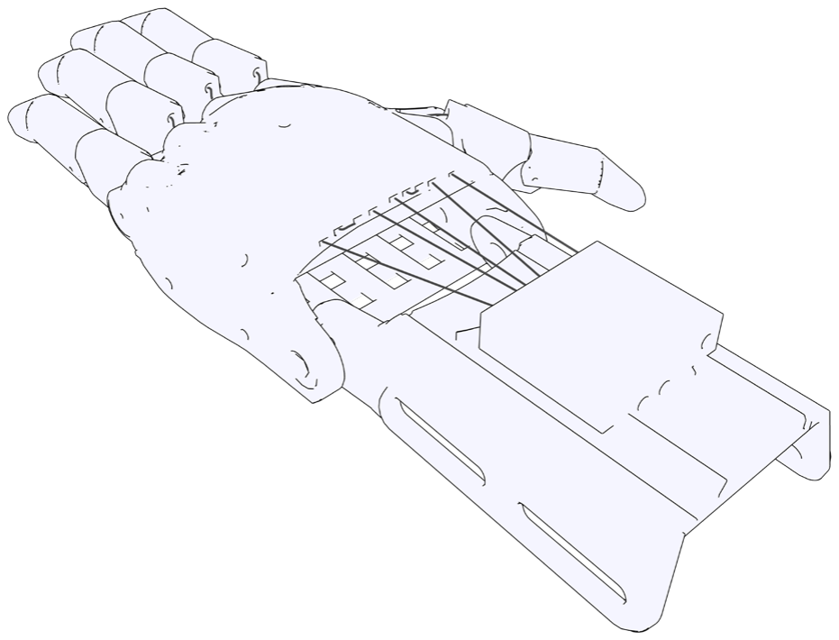
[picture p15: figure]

# Parts Required

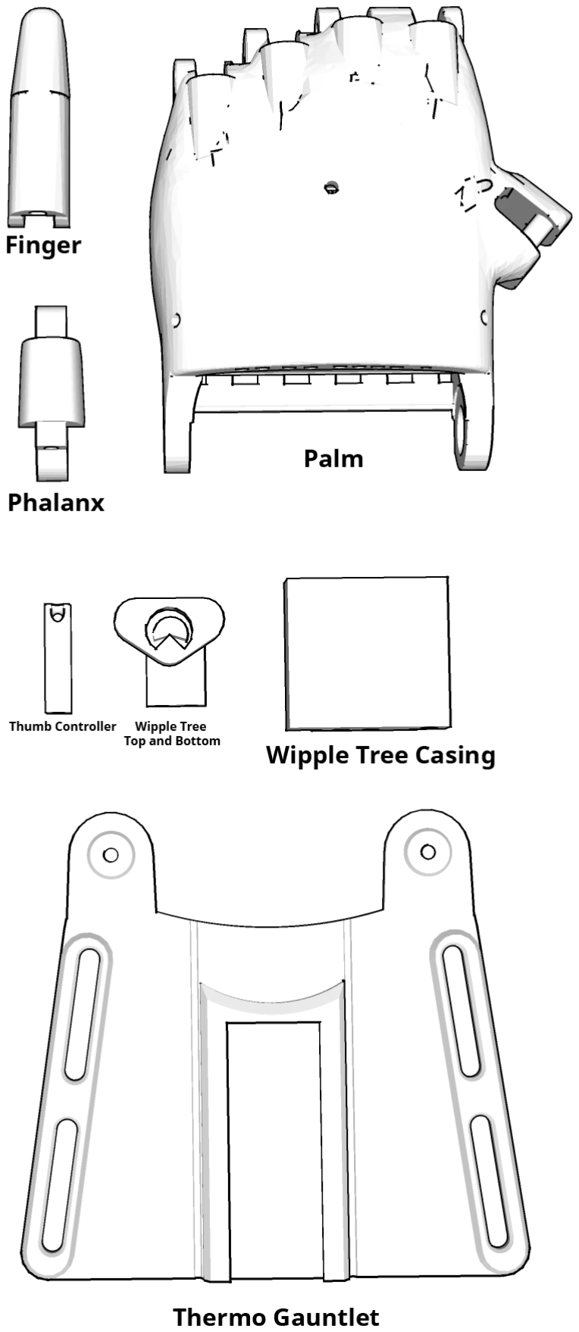
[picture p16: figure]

# Information Necessary for Assembly

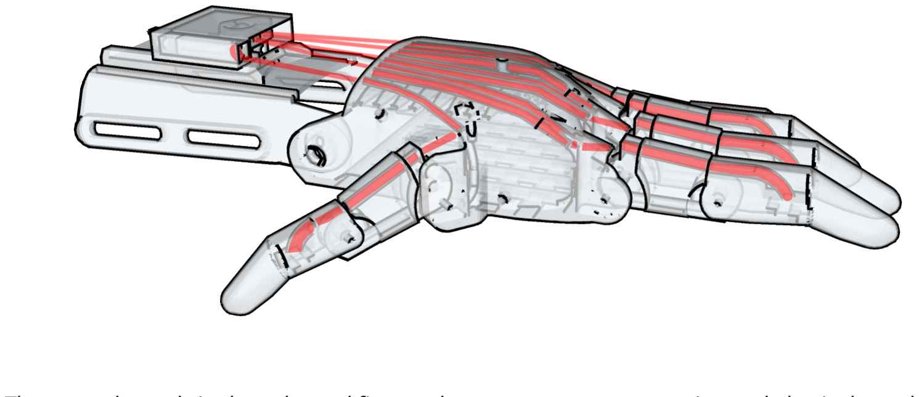
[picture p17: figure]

There are channels in the palm and fingers that are meant to route string and elastic through. The illustration above highlights these channels in red.

# Thermoforming the Thermo-Gauntlet

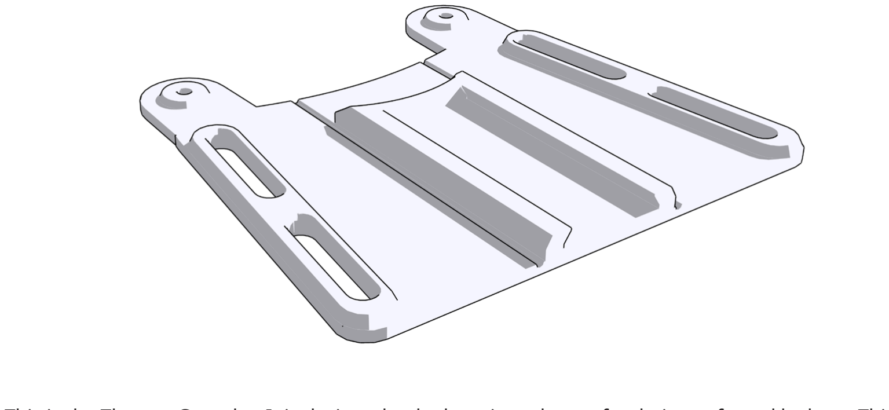
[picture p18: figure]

This is the Thermo Gauntlet. It is designed to be bent into shape after being softened by heat. This provides extra structural rigidity.

To Form the Thermo Gauntlet we need to apply heat, and then shortly afterward bend it into shape. It is recomended that you have a 2x4 wooden plank to use as a forming jig. We have found that it provides the best shape.

# Thermoforming the Thermo-Gauntlet (Continued)

1

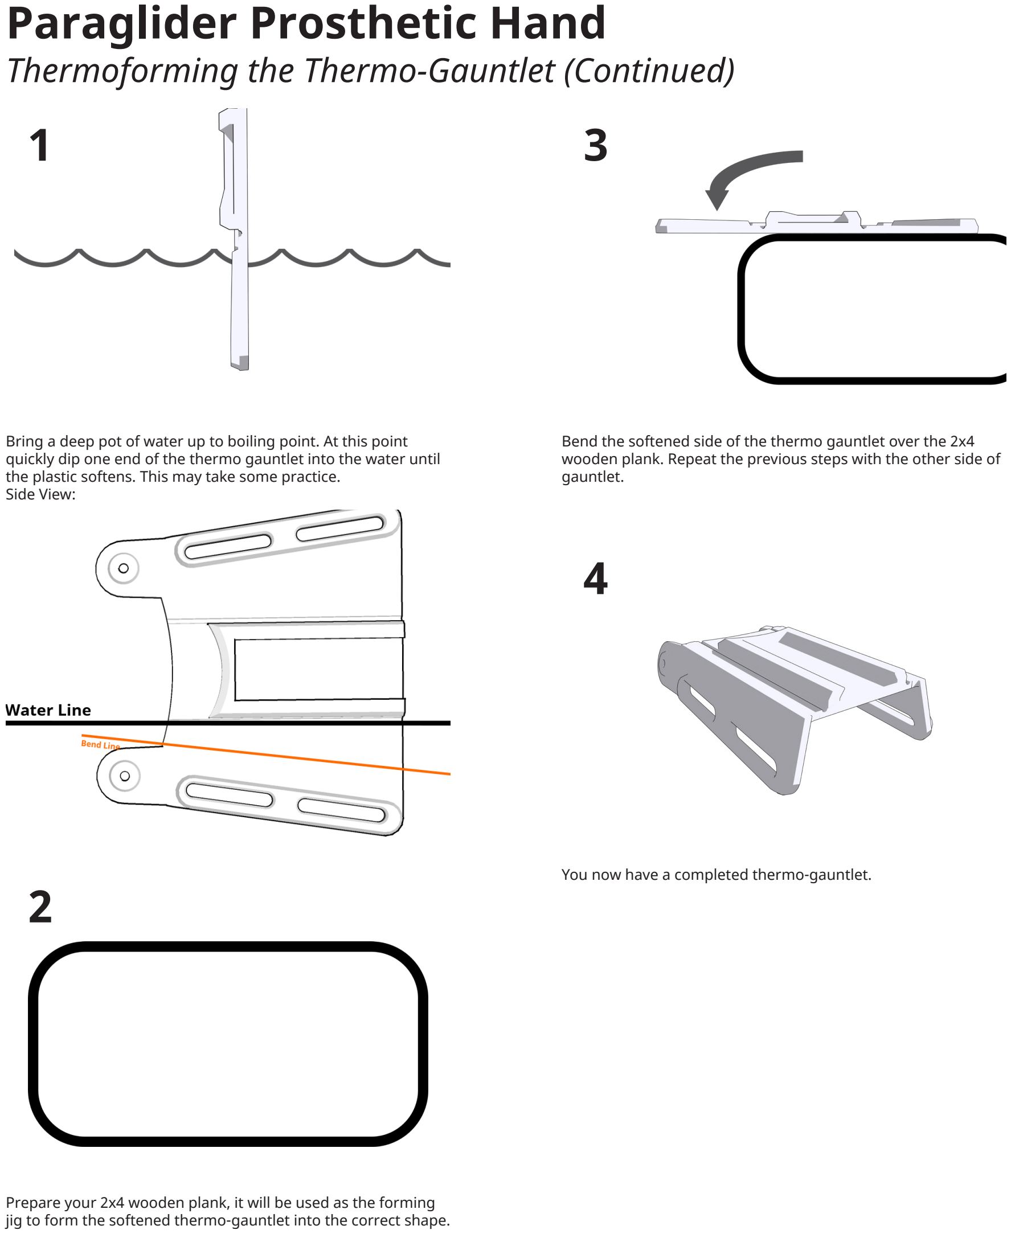
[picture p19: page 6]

Bring a deep pot of water up to boiling point. At this point quickly dip one end of the thermo gauntlet into the water until the plastic softens. This may take some practice.
Side View:

2

Prepare your 2x4 wooden plank, it will be used as the forming jig to form the softened thermo-gauntlet into the correct shape.

3

Bend the softened side of the thermo gauntlet over the 2x4 wooden plank. Repeat the previous steps with the other side of gauntlet.
4

You now have a completed thermo-gauntlet.

Attatching the Thermo-Gauntlet to the Palm.

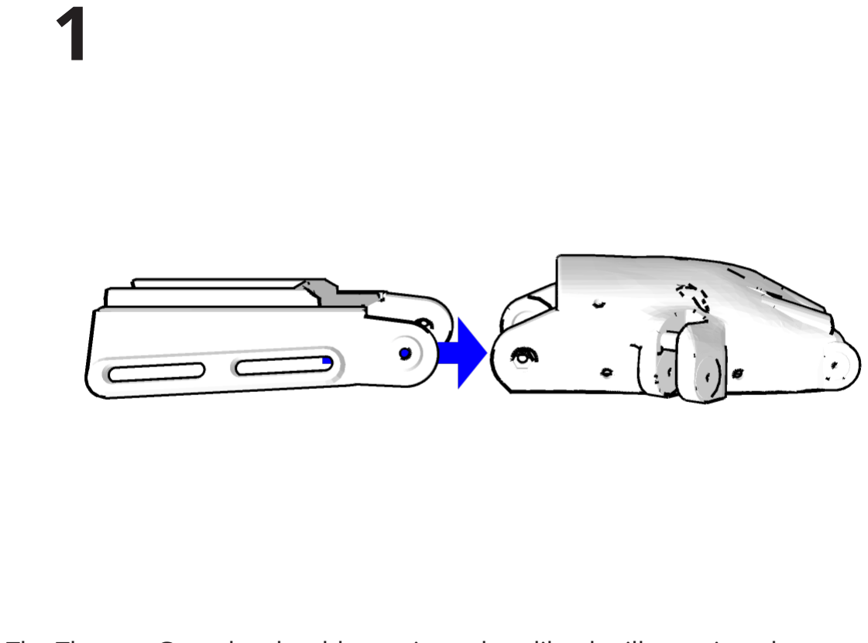
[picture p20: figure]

The Thermo-Gauntlet should snap into place like the illustration above.

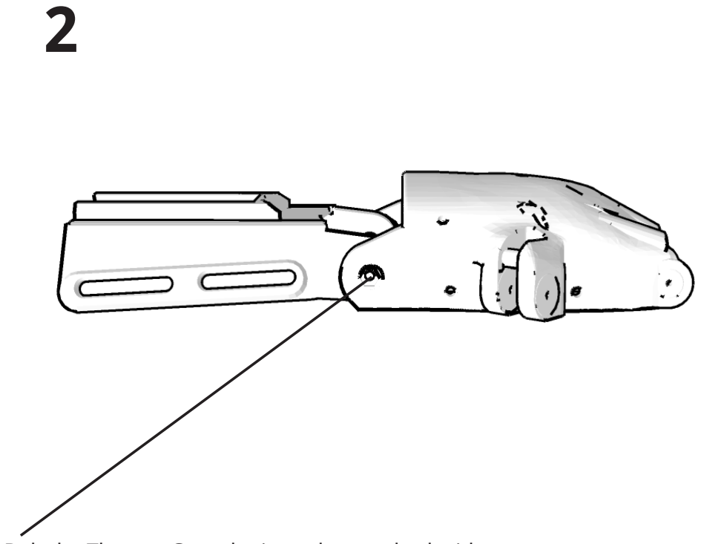
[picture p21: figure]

Bolt the Thermo Gauntlet into place on both sides.

# Stringing the Hand (Part one: Elastic)

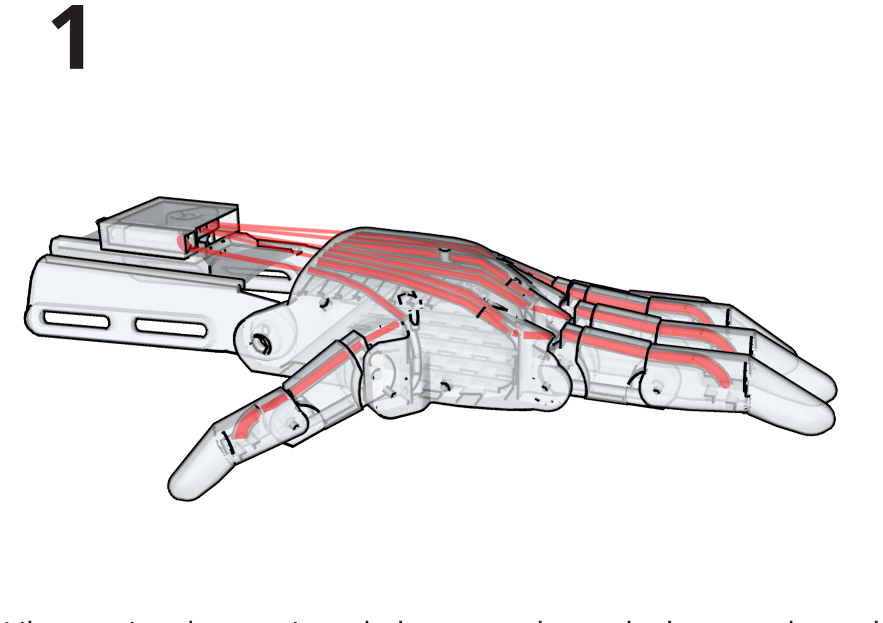
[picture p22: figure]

Like previously mentioned, there are channels that run through the palm and fingers that are meant to route strings and elastic cord through.

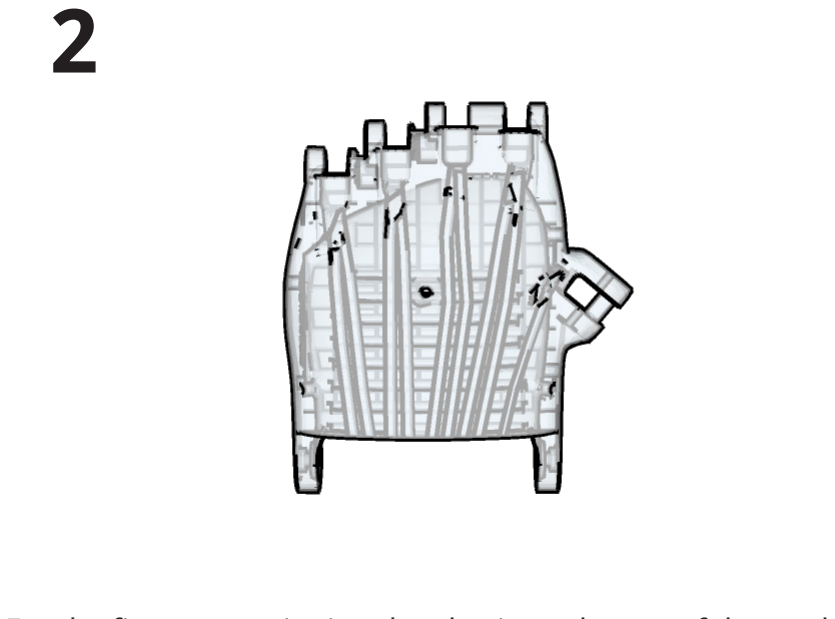
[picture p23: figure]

For the first part, stringing the elastic, and some of the cord, we will only need the palm.

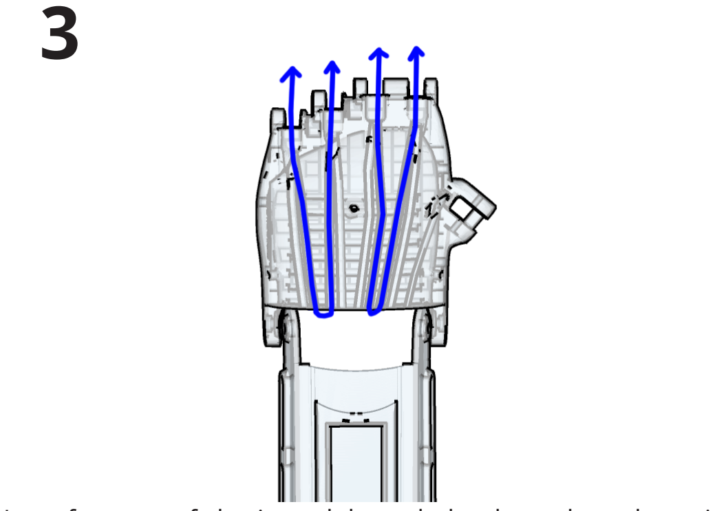
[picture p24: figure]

Loop four sets of elastic cord through the channels as shown in the illustration above. The blue color denotes the elastic. Make sure you have roughly 3 - 4 inches of elastic left over on both ends.

# Stringing the Hand (Part two: Cord + Gripper Box)

1

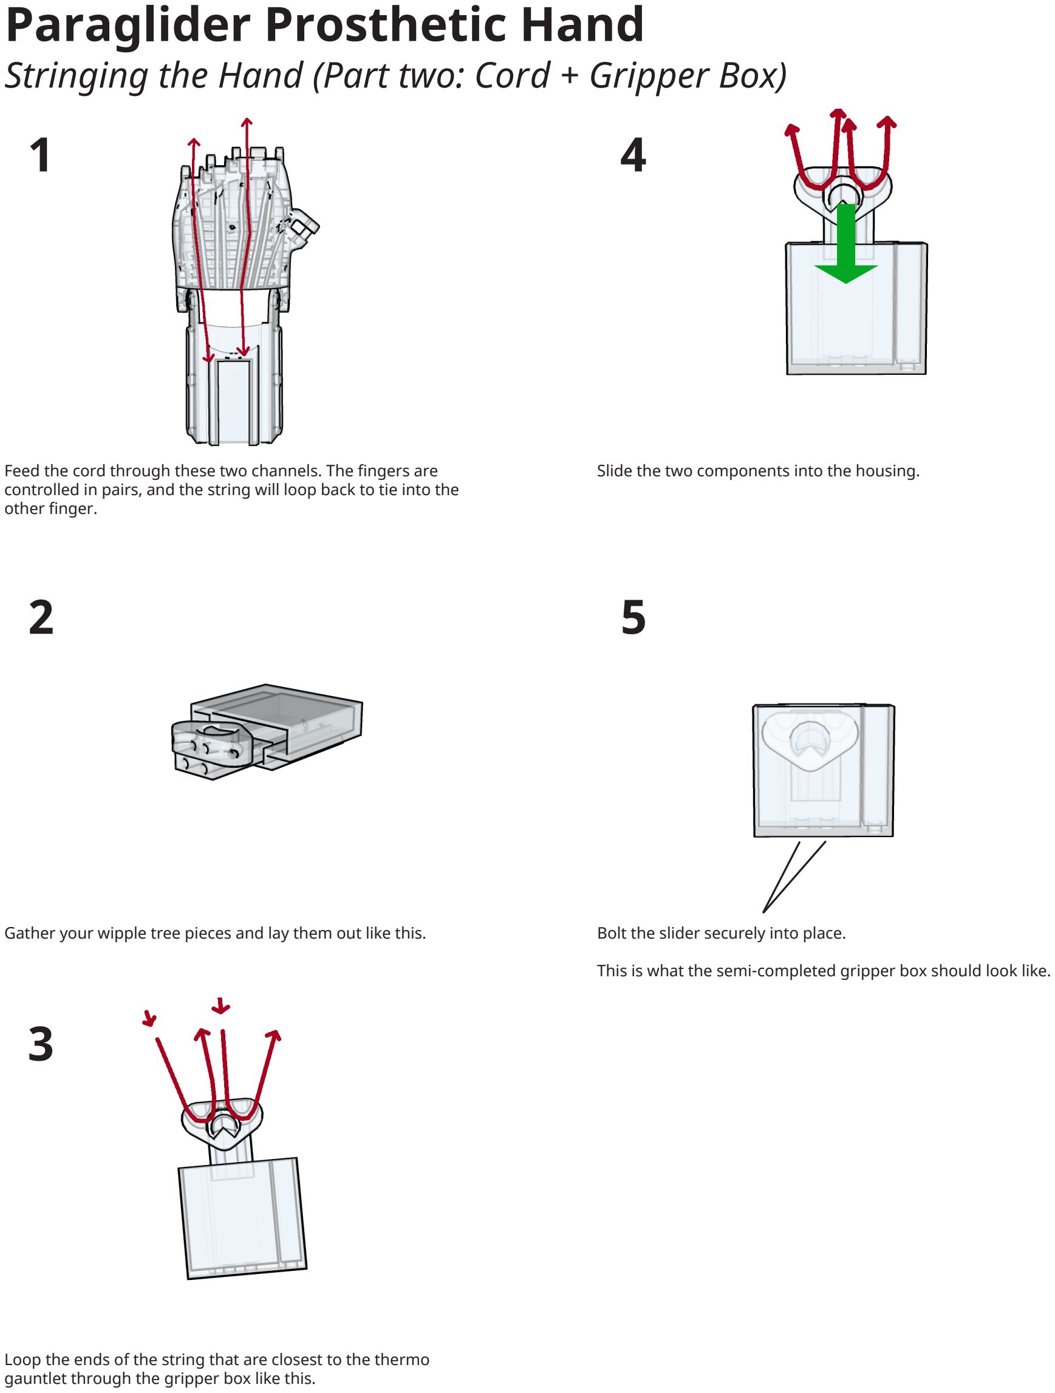
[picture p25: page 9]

Feed the cord through these two channels. The fingers are controlled in pairs, and the string will loop back to tie into the other finger.
2

Gather your wipple tree pieces and lay them out like this.
3

Loop the ends of the string that are closest to the thermo gauntlet through the gripper box like this.

4

Slide the two components into the housing.

5

Bolt the slider securely into place.
This is what the semi-completed gripper box should look like.

# Stringing the Hand (Part two: Cord + Gripper Box)

1

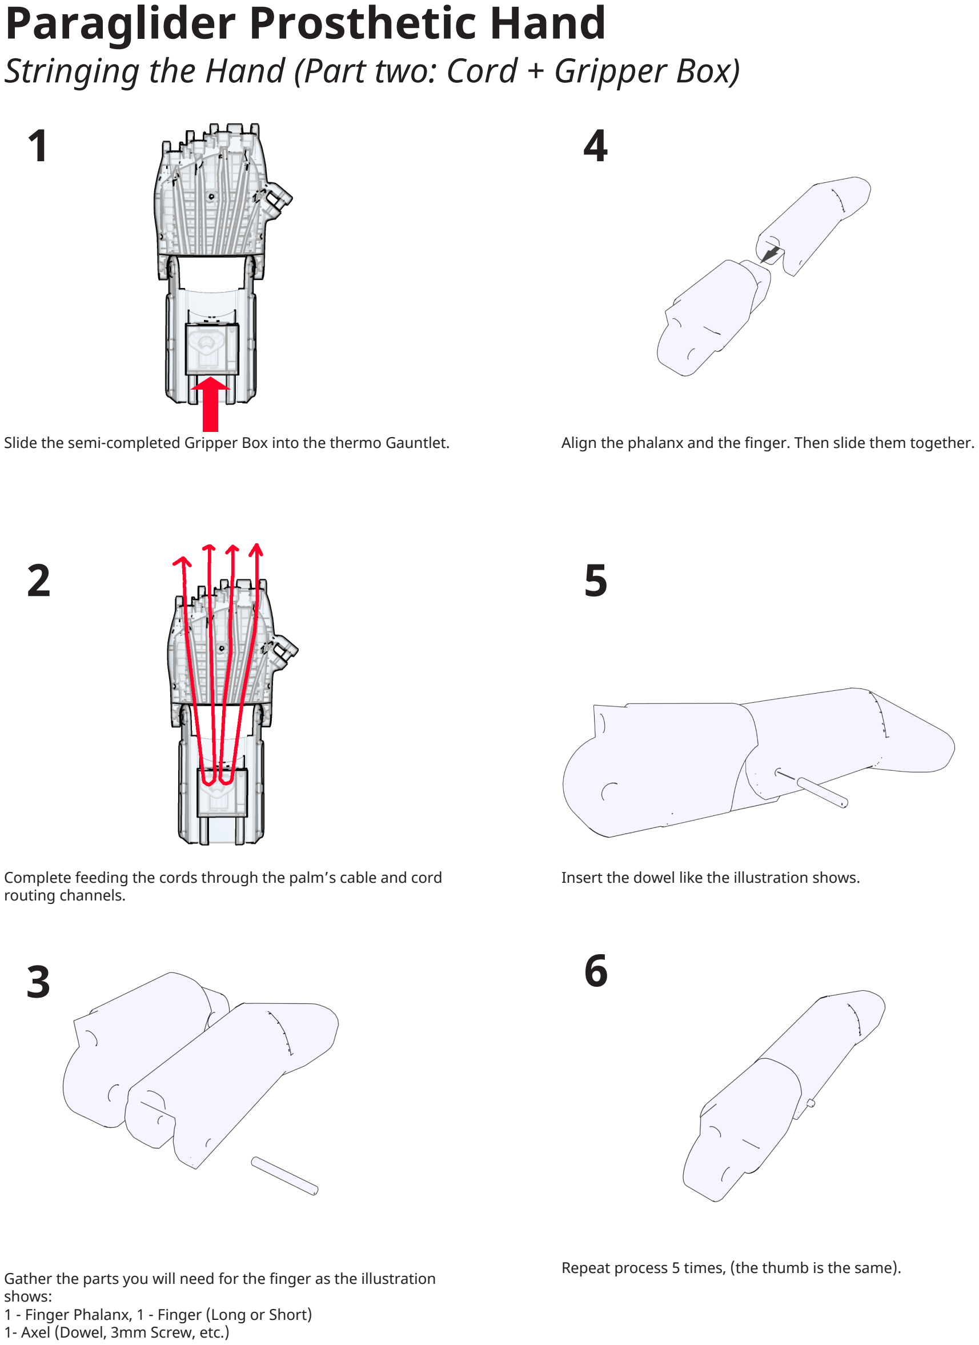
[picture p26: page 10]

Slide the semi-completed Gripper Box into the thermo Gauntlet.

2

Complete feeding the cords through the palm’s cable and cord routing channels.
3

Gather the parts you will need for the finger as the illustration shows:
1 - Finger Phalanx, 1 - Finger (Long or Short)
1- Axel (Dowel, 3mm Screw, etc.)

4

Align the phalanx and the finger. Then slide them together.

5

Insert the dowel like the illustration shows.
6

Repeat process 5 times, (the thumb is the same).

# Stringing the Hand (Part two: Cord + Gripper Box)

1

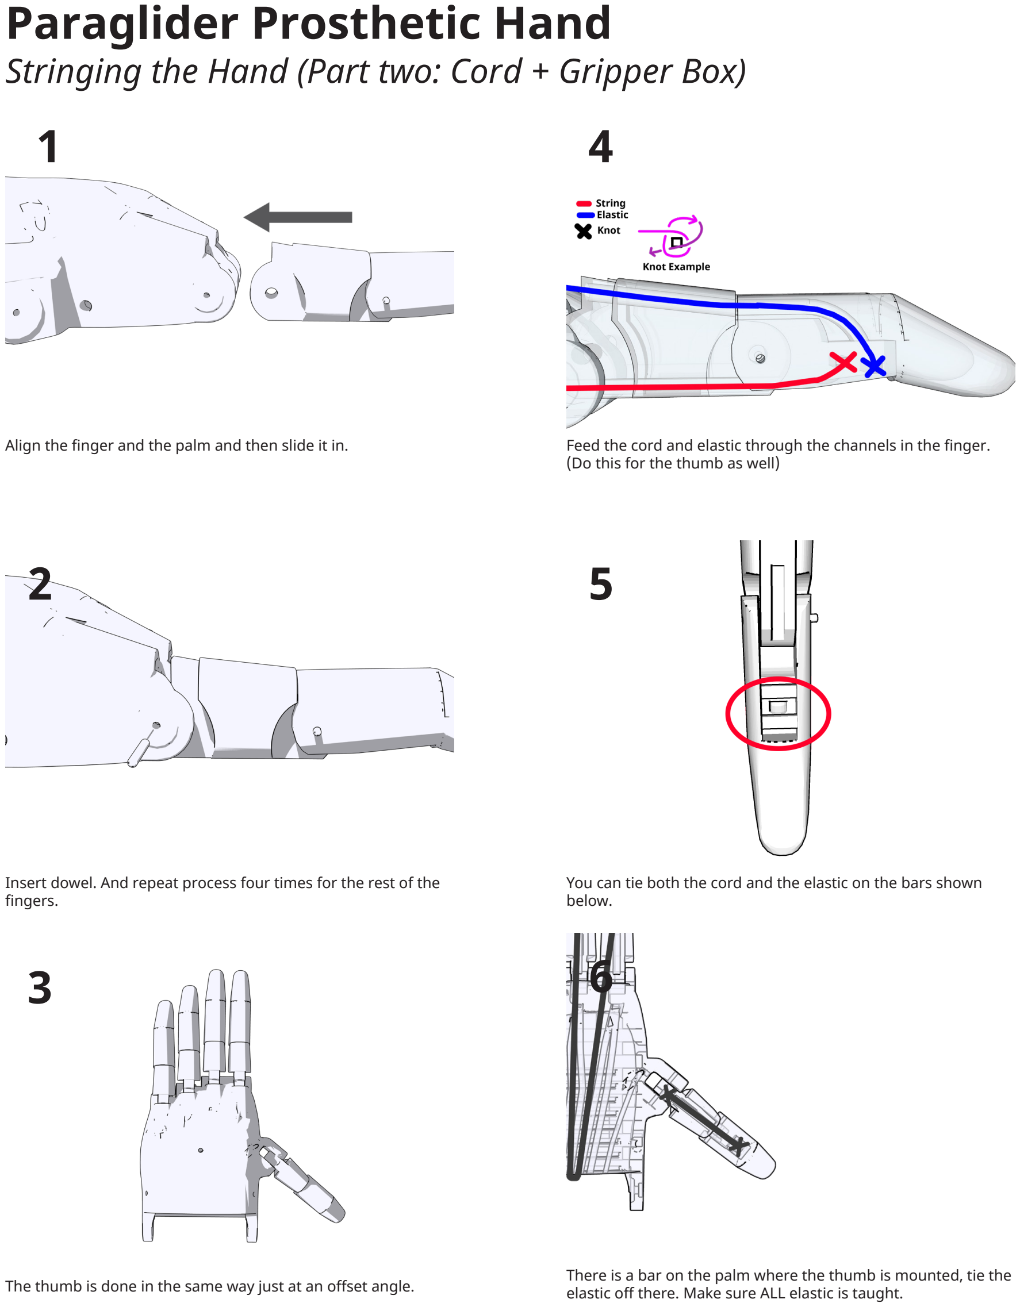
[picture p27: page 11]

Align the finger and the palm and then slide it in.

2

Insert dowel. And repeat process four times for the rest of the fingers.
3

The thumb is done in the same way just at an offset angle.

4

Feed the cord and elastic through the channels in the finger. (Do this for the thumb as well)
5

You can tie both the cord and the elastic on the bars shown below.
6

There is a bar on the palm where the thumb is mounted, tie the elastic off there. Make sure ALL elastic is taught.

# Stringing the Hand

1

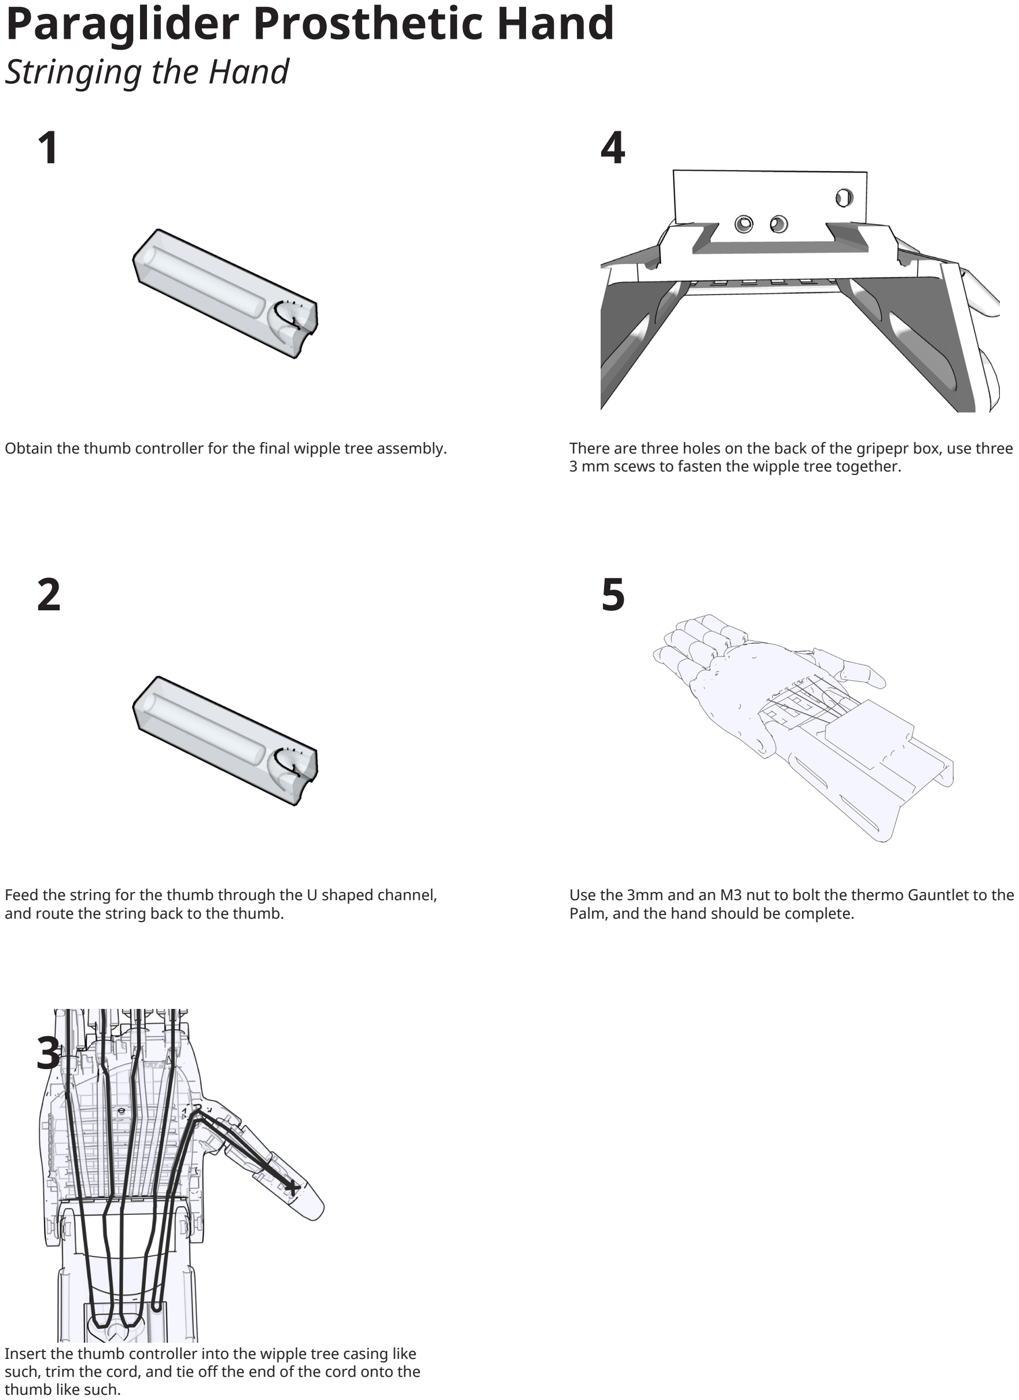
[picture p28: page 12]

Obtain the thumb controller for the final wipple tree assembly.

2

Feed the string for the thumb through the U shaped channel, and route the string back to the thumb.

3

Insert the thumb controller into the wipple tree casing like such, trim the cord, and tie off the end of the cord onto the thumb like such.

4

There are three holes on the back of the gripepr box, use three 3 mm scews to fasten the wipple tree together.
5

Use the 3mm and an M3 nut to bolt the thermo Gauntlet to the Palm, and the hand should be complete.

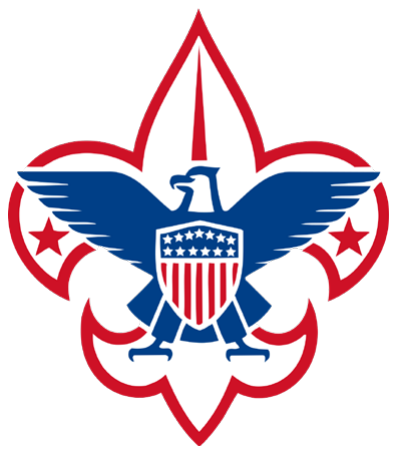
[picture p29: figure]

# Created by:

# Peter Ilyin’s Eagle Scout Project

## Special Thanks to Mr. Chang for being my Eagle Scout Project Coach, and his numerous advices

given.

## Special Thanks to Professor Dr. Marcus Mendenhall

for his time and endless patience.

## Special thanks to the volunteers of this project: Jackson Rodgers Leonard Katowitz Dean Deseve Albert Z Thomas H Dalton S Indigo S Chris S Rick Y Jasper Mosley Mark Dorazelski

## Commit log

2020-06-28 initial repo
    [fingerator.scad, gripper_box_pieces.scad, m4_wrist_assembly.scad, paraglider_palm_left.scad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]
2020-06-28 merged in Unlimbited palm
    [Unlimbited_v3_left_better_supp.scad, Unlimbited_v3_palm_left_f360.stl]
2020-06-28 removed many redundant files
    [Reborn_finger_phalanx.stl, Reborn_fingertip_pin.stl, Reborn_knuckle_pin_long.stl, Reborn_knuckle_pin_short.stl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]
2020-06-28 added v2 palm with new supports
    [Phoenix_v2_new_supports.stl]
2020-06-28 added customizer comments
    [gripper_box_pieces.scad]
2020-06-28 extraneous stl gone
    [gripper_box_left.stl]
2020-06-28 more instructions in README.md
    [swivel_pin_left_JD1.stl, thumb_v2_tensioner_pin.stl]
2020-06-29 customizer updates
    [fingerator.scad]
2020-10-12 added parametric string channel generation and separate channels for elastic and string to prepare for insertion of teflon tubing in string channels to reduce friction. Also, did better job filling i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
    [paraglider_palm_new_channels.scad]
2020-10-12 slight change to print plate layout
    [gripper_box_pieces.scad]
2020-10-13 added option for more aesthetic fingertips to fingerator. Covers string path on top of fingers, but requires a bit of threading work to pull elastic through to bottom where it ties off
    [fingerator.scad]
2020-10-15 first draft of file to generate fimgers without using original Phoenix fingertip
    [modeled_finger.scad]
2020-10-15 added support to make overhang print better. Alignment of channel on thumb is still not right.
    [modeled_finger.scad]
2020-10-15 added extra elastic clearance on end of thumb phalanx
    [modeled_finger.scad]
2020-10-16 made better customizer menu for pin type
    [modeled_finger.scad]
2020-10-16 made better customizer menu for pin type and clearance
    [modeled_finger.scad]
2020-10-18 old fingerator gone
    [fingerator.scad, modeled_finger.scad]
2020-10-19 pipe was missing
    [pipe.scad]
2020-10-21 added selections of which parts to generate in customizer, and added part of future modifications to work with plastic thrust bearings
    [fingerator.scad]
2020-10-21 customizer cleanup
    [fingerator.scad]
2020-10-22 cleaned up some sizes of oversized cutters and intersections which made it difficult to view in thrown-together mode
    [paraglider_palm_new_channels.scad]
2020-10-24 added simpler bottom mesh, prints faster and is stronger
    [paraglider_palm_new_channels.scad]
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2020-10-28 start of work on openscad gauntlet to allow better hinges
    [thermo_gauntlet.scad]
2020-10-28 remove sharp edge on track
    [thermo_gauntlet.scad]
2020-10-29 enlarges passages in fingers with rounded bottom to make compatible with 1/16" silicone oring material for elastic
    [fingerator.scad]
2020-10-31 added knuckle covers
    [paraglider_palm_new_channels.scad]
2020-10-31 clean up knuckle covers
    [paraglider_palm_new_channels.scad]
2020-10-31 clean up string guides slightly
    [paraglider_palm_new_channels.scad]
2020-11-01 much better routing for thumb string
    [paraglider_palm_new_channels.scad]
2020-11-01 much better routing for thumb string and support for new hanging hole from this passage
    [paraglider_palm_new_channels.scad]
2020-11-01 added spherical joint on thumb string to reduce internal edges
    [paraglider_palm_new_channels.scad]
2020-11-03 further thumb plumbing cleanup, and new pic
    [paraglider_palm_new_channels.scad]
2020-11-04 file renaming
    [paraglider_palm_left.scad, paraglider_palm_left_outdated.scad, paraglider_palm_new_channels.scad]
2020-11-04 added extra passage drilling to make threading fingers easier
    [paraglider_palm_left.scad]
2020-11-04 separate scaling of elastic channels and string cnahhels, but need to adjust coordinates to kep channel bottoms at the same position, instead of the middle.
    [paraglider_palm_left.scad]
2020-11-04 fixed translation and scaling of tunnels to keep bottoms fixed
    [paraglider_palm_left.scad]
2020-11-04 translation fix broke plugging of old channels; it is not a option on the channel driller, so it is on for new channels and off for plugging old ones
    [paraglider_palm_left.scad]
2020-11-04 reduced depth of finger stops to make stringing easier
    [paraglider_palm_left.scad]
2020-11-05 trying to fix pre-solidifed palm... still doesnt work, not valid mesh, dont use
    [paraglider_palm_left.scad]
2020-11-06 added ability to use Unlimbited v3 palm. Not quite ready to go, but very close.
    [palm_v3.3mf, paraglider_palm_v3.scad]
2020-11-06 v3 palm almost ready to go. all old channels plugged,and new routes seem good.
    [paraglider_palm_v3.scad]
2020-11-07 lots of cleanup
    [paraglider_palm_v3.scad]
2020-11-08 added ability to use simplisifed mesh to v3 palm
    [paraglider_palm_unlimbited_v3.scad]
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2020-11-11 cleaner string and elastic transitions
    [paraglider_palm_unlimbited_v3.scad]
2020-11-24 heavy restructuring of code to almost pure functional programming to improve module isolation
    [paraglider_palm_unlimbited_v3.scad]
2020-11-24 fixed scaling of m3 wrist screw parts
    [paraglider_palm_unlimbited_v3.scad]
2020-11-24 working towards m3 pinned wrist
    [paraglider_palm_unlimbited_v3.scad, thermo_gauntlet.scad]
2020-11-26 capable of using m3 screws on wrists, now, but this isnt fully tested
    [paraglider_palm_unlimbited_v3.scad, thermo_gauntlet.scad]
2020-11-26 capable of using m3 screws on wrists, now, but this isnt fully tested, slight bearing cleanup on gauntlet
    [thermo_gauntlet.scad]
2020-11-26 improved conical bearing design for better seating
    [thermo_gauntlet.scad]
2020-11-27 dovetail now fits correctly. also, put in correct Customizer annotations
    [thermo_gauntlet.scad]
2020-11-27 added machining of wrist tabs so the surfaces are perfectly vertical and parallel
    [paraglider_palm_unlimbited_v3.scad]
2020-11-28 added whipple tree to gripper box parts
    [gripper_box_pieces.scad]
2020-11-29 improved whippe tree layout
    [gripper_box_pieces.scad]
2020-11-29 cleanup parts layout
    [gripper_box_pieces.scad]
2020-11-30 added option to fingers for a steel pin to tie string to, instead of printed plastic bars
    [fingerator.scad]
2020-12-02 added pins without bearings to phalanges which works very well will nylon or Dow OBC filament for phalanges only, probably OK too with regular PLA etc., but not as smooth
    [fingerator.scad]
2020-12-02 no longer needed
    [whippletree_JD3.stl]
2020-12-02 removed whippletree_JD3.stl, it is no longer needed since the gripper_box_pieces.scad file now generates this.
    [paraglider_palm_left_outdated.scad, paraglider_palm_v3.scad, whippletree_JD3.stl]
2020-12-05 swapped old, non-operator based file for v2 palm out for operator-based file, like v3.
    [paraglider_palm_left.scad, paraglider_palm_left_old.scad]
2020-12-05 added optional stamping die for wrist bearing
    [paraglider_palm_left.scad]
2020-12-05 eliminated stray micro-holes do to misalignment of fill-in cylinders for mesh screw holes
    [paraglider_palm_left.scad]
2020-12-05 eliminated stray micro-holes due to misalignment of fill-in cylinders for mesh screw holes
    [paraglider_palm_left.scad]
2020-12-05 fixed off-center screw holes in gripper box pivot
    [gripper_box_pieces.scad]
2020-12-06 timy fiddling with channelsin v2 palm
    [paraglider_palm_left.scad]
2020-12-06 fixed minor oops with new channels
    [paraglider_palm_left.scad]
2020-12-06 more fixes, removed tiny void on pinkie channel fill-in
    [paraglider_palm_left.scad]
2020-12-06 also fixed micro-voids in channel filling in v3 palm
    [paraglider_palm_unlimbited_v3.scad]
2020-12-09 added stmping die for bearing to v3, too.
    [paraglider_palm_unlimbited_v3.scad]
2020-12-09 added drill-guide hole in bearing forming die so nice, centered hole can be driller after shaping the bearing
    [paraglider_palm_left.scad, paraglider_palm_unlimbited_v3.scad]
2020-12-09 Delete reborn_fingertip_long_front.3mf
    no longer needed with fingerator generating the tip
    [reborn_fingertip_long_front.3mf]
2020-12-09 Delete m4_wrist_assembly.scad
    wrist assembly based on m3 screw integrated into palms.
    [m4_wrist_assembly.scad]
2020-12-09 Delete paraglider_palm_left_old.scad
    no need
    [paraglider_palm_left_old.scad]
2020-12-09 cleaned up forming dies, added size label in case they want to be reused
    [paraglider_palm_left.scad, paraglider_palm_unlimbited_v3.scad]
2020-12-10 added labeling to v3 palm
    [paraglider_palm_unlimbited_v3.scad]
2020-12-10 labels have 3 lines
    [paraglider_palm_unlimbited_v3.scad]
2020-12-10 fixed customizer
    [paraglider_palm_unlimbited_v3.scad]
2020-12-10 much cleanup on text labeling
    [paraglider_palm_unlimbited_v3.scad]
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2020-12-11 added text to v2 palm, too, and fixed up customizer to be just like v3. cleanup on both
    [paraglider_palm_left.scad, paraglider_palm_unlimbited_v3.scad]
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2020-12-14 fixed counting error on facets in pipe.scad which was resulting in degenerate polygon warnings
    [pipe.scad]
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
